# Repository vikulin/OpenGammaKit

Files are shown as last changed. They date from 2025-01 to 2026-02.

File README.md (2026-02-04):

# OpenGammaKit

## PCB front and back side

<table>
  <tr>
    <td align="center">
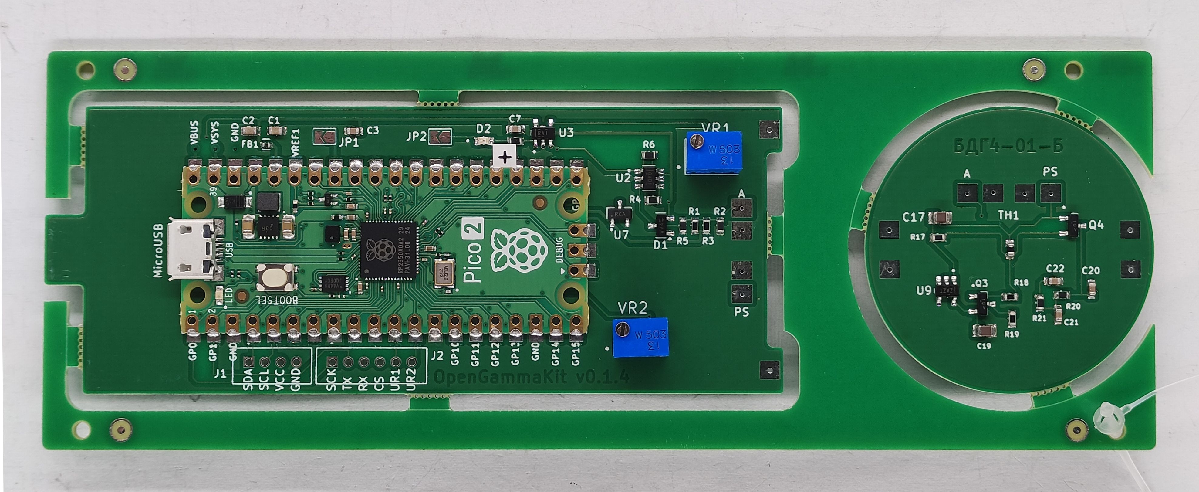
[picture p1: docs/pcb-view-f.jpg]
Front View of the detector board Front View
      
      <br><b>Front view</b>
    </td>
    <td align="center">
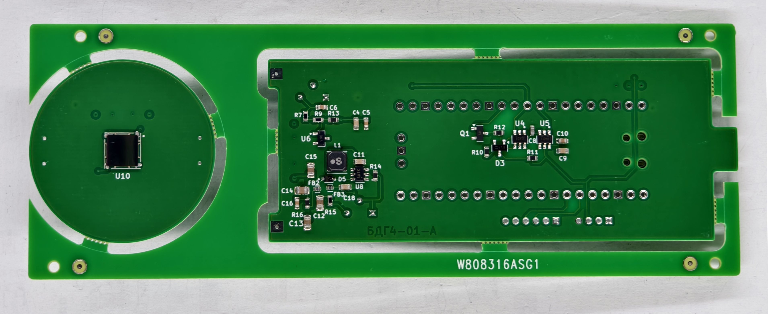
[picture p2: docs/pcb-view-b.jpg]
Back View of the detector board Back View
      
      <br><b>Back view</b>
    </td>
  </tr>
</table>

**OpenGammaKit** is an open-source gamma spectrometer hardware platform, inspired by the excellent [Open-Gamma-Detector](https://github.com/OpenGammaProject/Open-Gamma-Detector). It takes the original schematic and redesigns the PCB using **KiCad** (originally designed in EasyEDA), making the project more accessible and modifiable for open hardware enthusiasts.

OpenGammaKit is designed to be affordable, reliable, and easy to integrate with embedded systems, mobile devices, or PCs—ideal for DIY nuclear instrumentation, educational labs, or citizen science.

---

## Order the PCB or PCB + Assembly

You can order the **Open Gamma Kit** PCB or a fully assembled board directly from PCBWay using the link below:

Order from PCBWay (https://www.pcbway.com/project/shareproject/W808316ASG1_open_gamma_kit_gerber_files_v0_1_4_2_90620442.html)

👉 [Order PCB or PCB + Assembly from PCBWay](https://www.pcbway.com/project/shareproject/W808316ASG1_open_gamma_kit_gerber_files_v0_1_4_2_90620442.html)

This helps support the project and ensures high-quality manufacturing.

---

## 🔧 Features

- ✅ Based on the **Open-Gamma-Detector** schematic  
- ✅ Complete redesign in **KiCad** with improved layout and routing  
- ✅ USB serial communication (compatible with Android 7.0+ and PCs)  
- ✅ Compatible with [OGK Inspector](https://github.com/vikulin/OGK-Inspector) Android app and [OGK Firmware](https://github.com/vikulin/OGK-Firmware) 
- ✅ Real-time gamma spectrum output and spectrometer integration  
- ✅ Works with scintillation detectors (e.g., CsI(Tl), NaI(Tl), etc.)  
- ✅ Open and editable source files for schematics and PCB

---

## 📘Assembly guide, 3D models for enclosure

https://github.com/vikulin/OGK-3D-Models

---

## 📂 Repository Contents

- `/docs/` – Spectrum([OGK Inspector](https://github.com/vikulin/OGK-Inspector))
- `/kicad-libraries/` – KiCad libraries, including custom footprints

---

## 📷 3D render previews of the boards

<p align="center">
  <br>
  3d Front View of the detector board
  <br>
  3d Back View of the detector board
</p>

---

## 📦 Release Contents

OpenGammaKit releases version **0.1.5.5** and later include all the fabrication files required to manufacture and assemble the OpenGammaKit gamma spectrometer hardware:

| File Name                                     | Description                                                                |
| --------------------------------------------- | -------------------------------------------------------------------------- |
| `open-gamma-kit-gerber-files-<version>.zip`   | 🟢 Complete Gerber and Drill files for PCB fabrication.                    |
| `open-gamma-kit-centroid-file-<version>.csv`  | 📍 Centroid (Pick-and-Place) file in mils for automated assembly.          |
| `open-gamma-kit-<version>.pdf`                | 📄 PDF documentation                                                       |
| `BOM.csv`                                     | 📋 Bill of Materials (not archived — listed separately).                   |

📁 **Location**: All files are available in the [Assets](https://github.com/vikulin/OpenGammaKit/releases) release section.

---

## 🧠 Companion Projects

- **OGK Inspector (Android App)**  
  View spectra, calculate resolution, access terminal mode  
  👉 [OGK-Inspector on GitHub](https://github.com/vikulin/OGK-Inspector)

- **OGK Firmware**  
  USB serial interface firmware for supported microcontrollers  
  👉 [OGK Firmware Repository](https://github.com/vikulin/OGK-Firmware)

---

## Spectrum of ²⁴¹Am source measured with NaI(Tl) detector
| Element | Symbol | Atomic Number | Mass Number |
|---------|--------|----------------|--------------|
| Americium | Am     | 95             | 241          |

The spectrum clearly shows two gamma peaks at **59.54 keV** and **26.35 keV**, both corresponding to emissions from ²⁴¹Am:

- The **59.54 keV** peak is the most intense and commonly used for energy calibration.
- The **26.35 keV** peak is weaker but still visible, depending on detector resolution and shielding conditions.

<p align="center">
  <br>
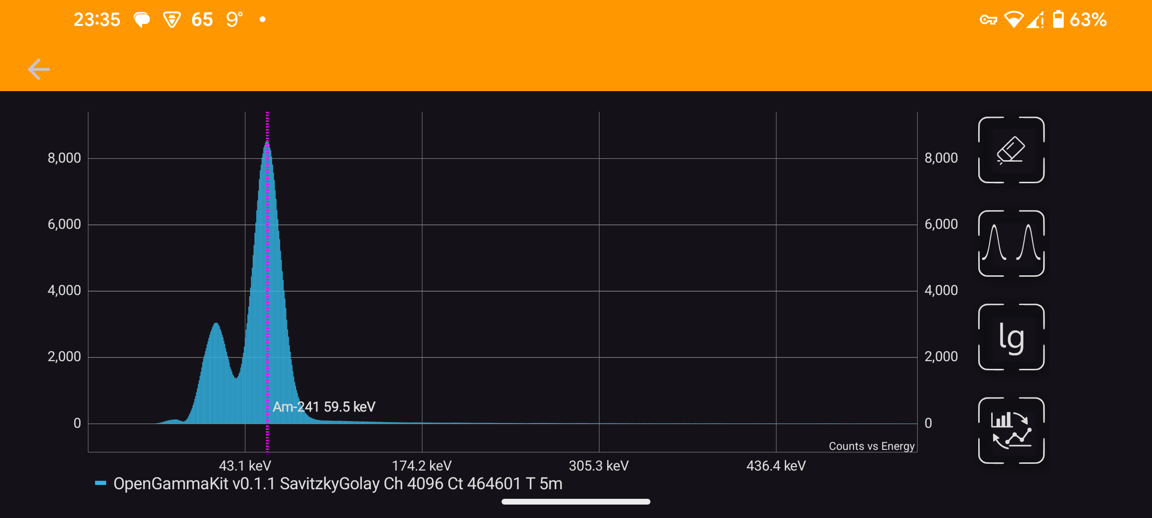
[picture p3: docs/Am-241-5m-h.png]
Am-241 Am-241 10 minutes spectrum
  
</p>

> 📌 These lines are useful for calibration and spectral identification in low-energy gamma spectroscopy using NaI(Tl) detectors.

---

## 📜 License

This project is licensed under the **GNU General Public License v3.0**.  
See the [LICENSE](LICENSE) file for details.

---

## 🙌 Acknowledgements

- Based on the original design by [OpenGammaProject](https://github.com/OpenGammaProject/Open-Gamma-Detector)  
- Thanks to the open hardware and spectroscopy communities!

---

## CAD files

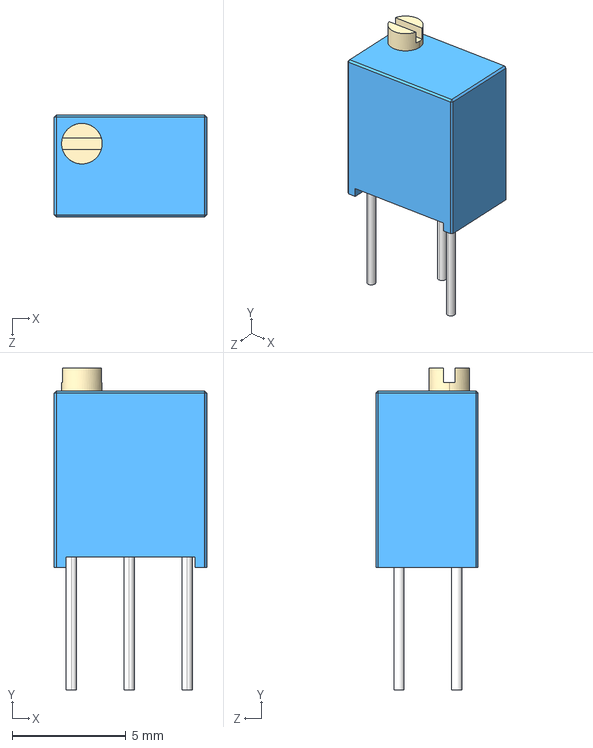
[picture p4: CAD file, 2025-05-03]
kicad-libraries/3266W-1-503/3266W-1-503.step
6.71 x 14.1 x 4.50 mm

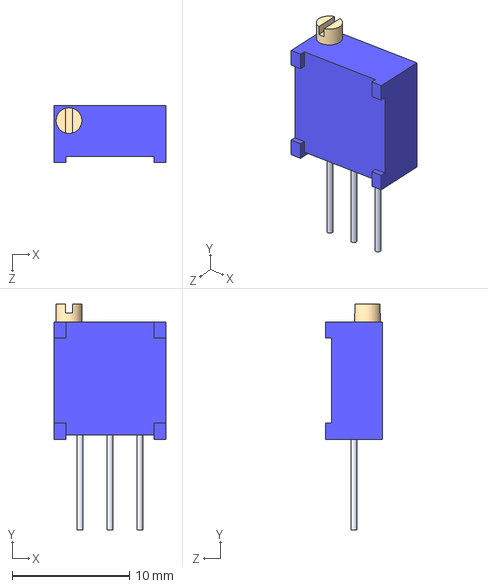
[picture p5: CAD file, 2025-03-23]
kicad-libraries/3296W-1-502LF/3296W-1-502LF.step
9.53 x 19.3 x 4.83 mm

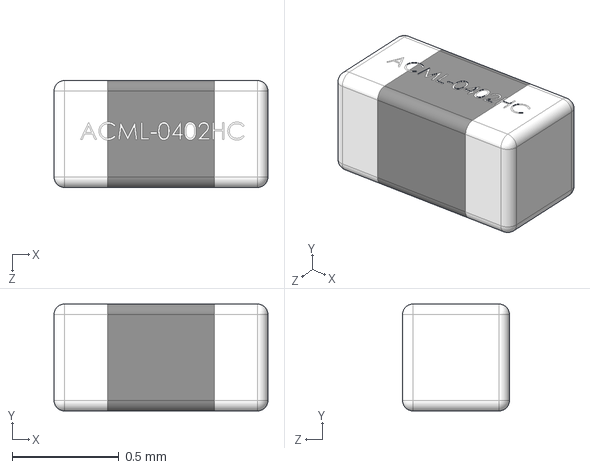
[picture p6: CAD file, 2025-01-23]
kicad-libraries/ACML-0402HC-301-T/ACML-0402HC-301-T.step
1.00 x 0.5 x 0.5 mm

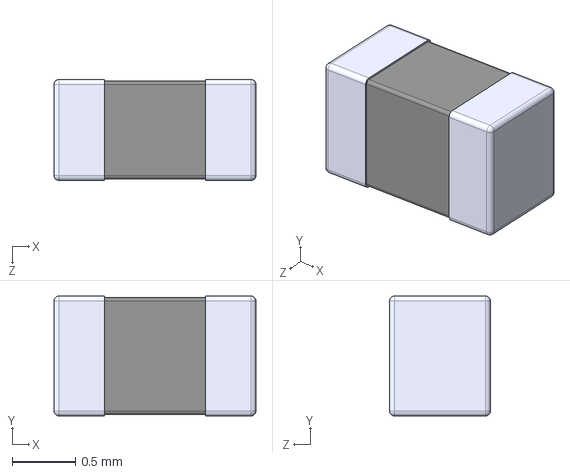
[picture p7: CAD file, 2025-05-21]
kicad-libraries/BLM18KG102SN1D/BLM18KG102SN1D.step
1.60 x 0.95 x 0.8 mm

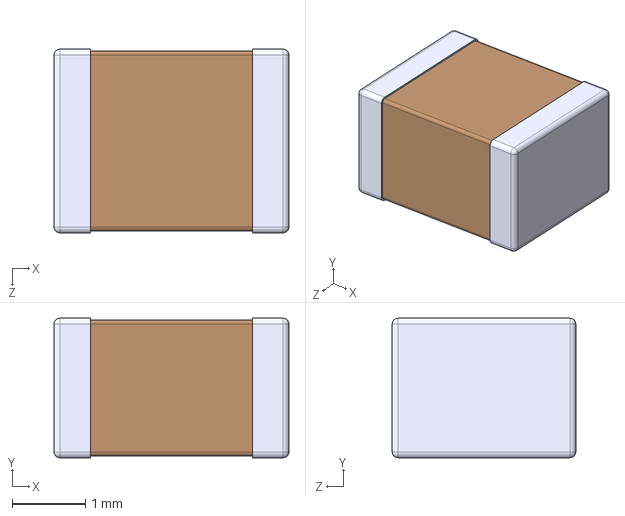
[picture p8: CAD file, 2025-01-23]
kicad-libraries/C1210C104KCRACTU/C1210C104KCRACTU.step
3.20 x 1.90 x 2.50 mm

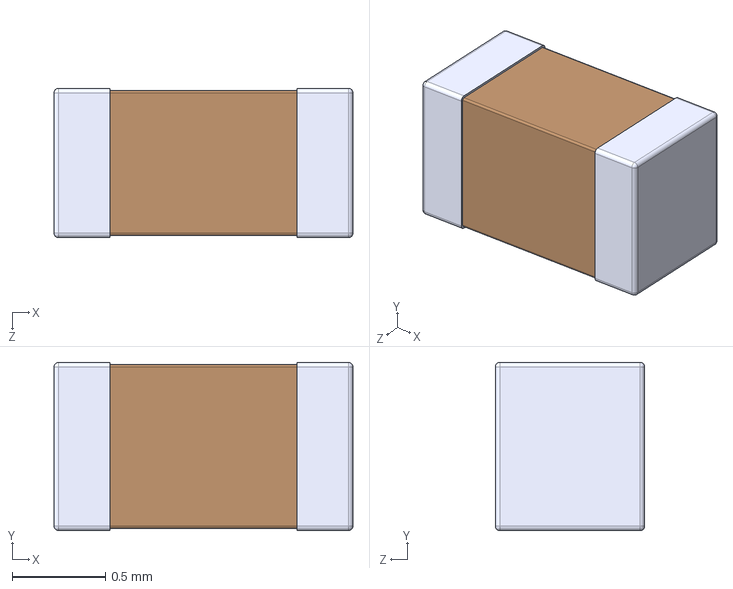
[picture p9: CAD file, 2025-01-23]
kicad-libraries/CL10A226MP8NUNE/CL10A226MP8NUNE.step
1.60 x 0.9 x 0.8 mm

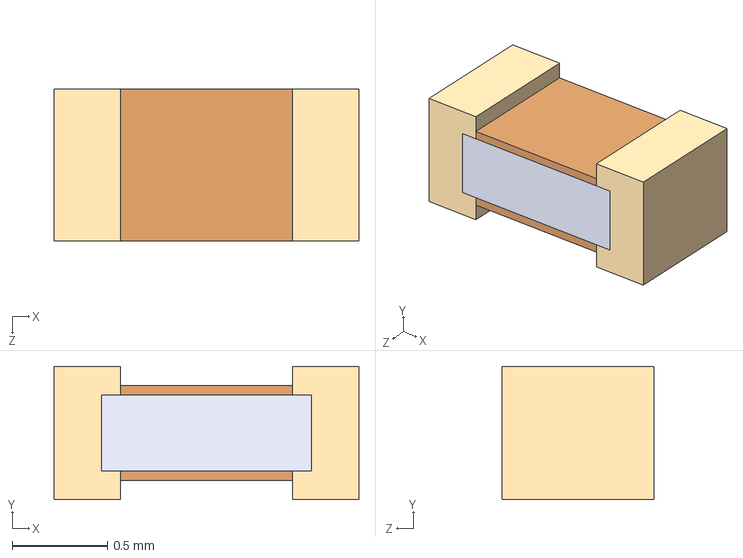
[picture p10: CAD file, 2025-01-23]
kicad-libraries/ECHU1C471JX5/ECHU1C471JX5.step
1.60 x 0.7 x 0.8 mm

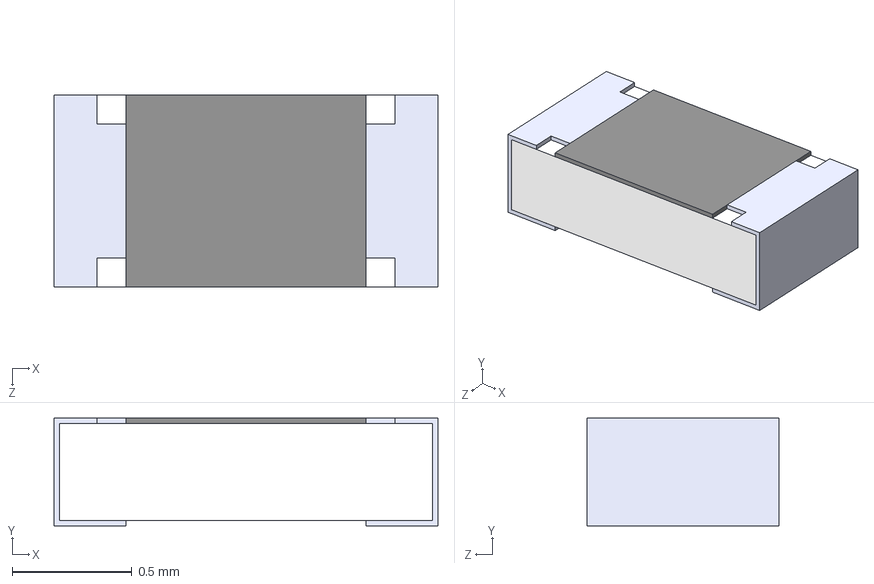
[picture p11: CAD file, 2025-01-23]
kicad-libraries/ERJ3EKF1000V/ERJ3EKF1000V.step
1.60 x 0.45 x 0.8 mm

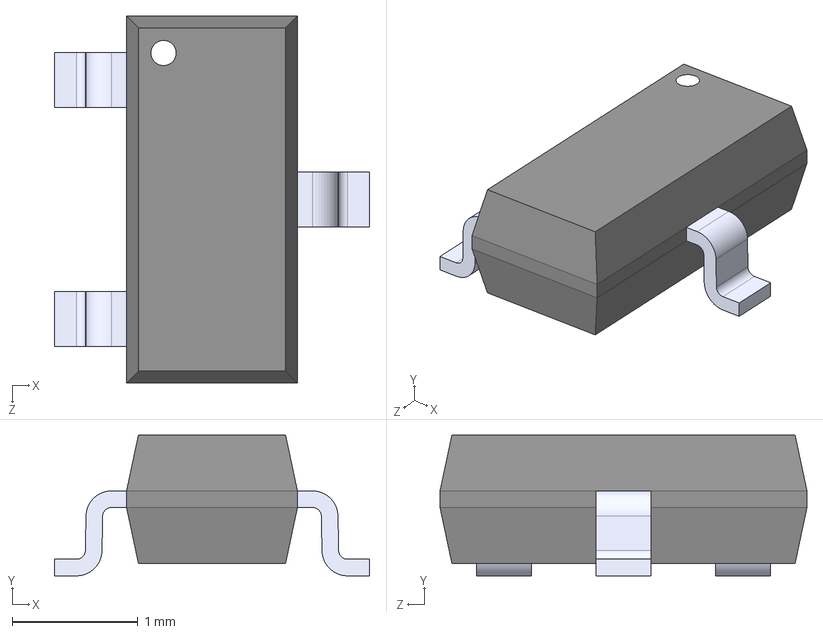
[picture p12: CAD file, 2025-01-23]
kicad-libraries/IRLML6344TRPBF/IRLML6344TRPBF.step
2.51 x 1.12 x 2.92 mm

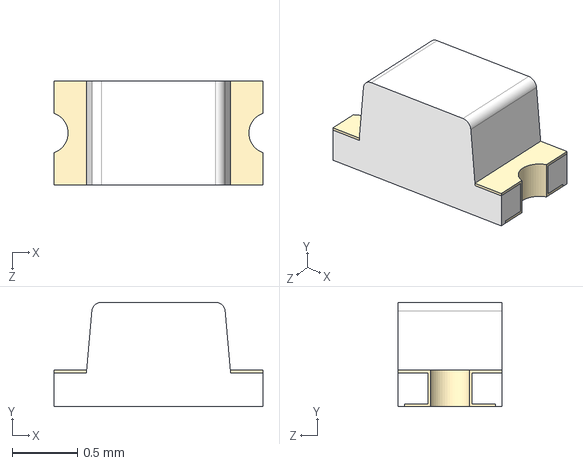
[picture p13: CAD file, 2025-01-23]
kicad-libraries/LTST-C190KGKT/LTST-C190KGKT.step
1.60 x 0.8 x 0.8 mm

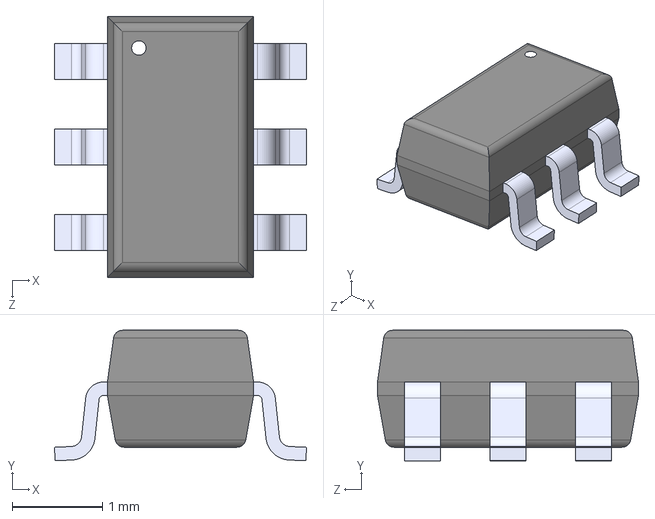
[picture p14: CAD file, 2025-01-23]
kicad-libraries/MAX5026EUT_T/MAX5026EUT_T.step
2.80 x 1.45 x 2.90 mm

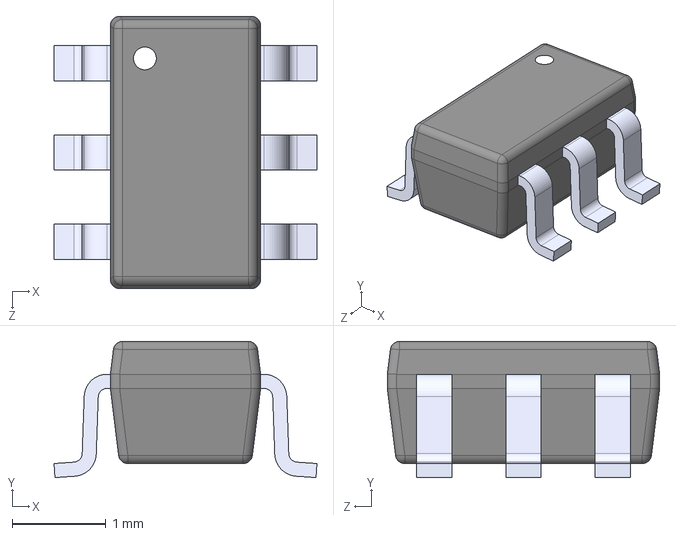
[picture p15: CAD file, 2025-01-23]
kicad-libraries/OPA357AIDBVR/OPA357AIDBVR.step
2.80 x 1.45 x 2.90 mm

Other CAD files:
kicad-libraries/20449-001E-03/20449-001E-03.step
kicad-libraries/MMBT5088LT1G/MMBT5088LT1G.step
kicad-libraries/NRS4018T470MDGJ/NRS4018T470MDGJ.step
kicad-libraries/TPS7B6950DBVR/TPS7B6950DBVR.step
kicad-libraries/TPS7B6950QDCYRQ1/TPS7B6950QDCYRQ1.step
kicad-libraries/ul_AST0760MCTRQ/AltiumDesigner/AST0760_MAL.step

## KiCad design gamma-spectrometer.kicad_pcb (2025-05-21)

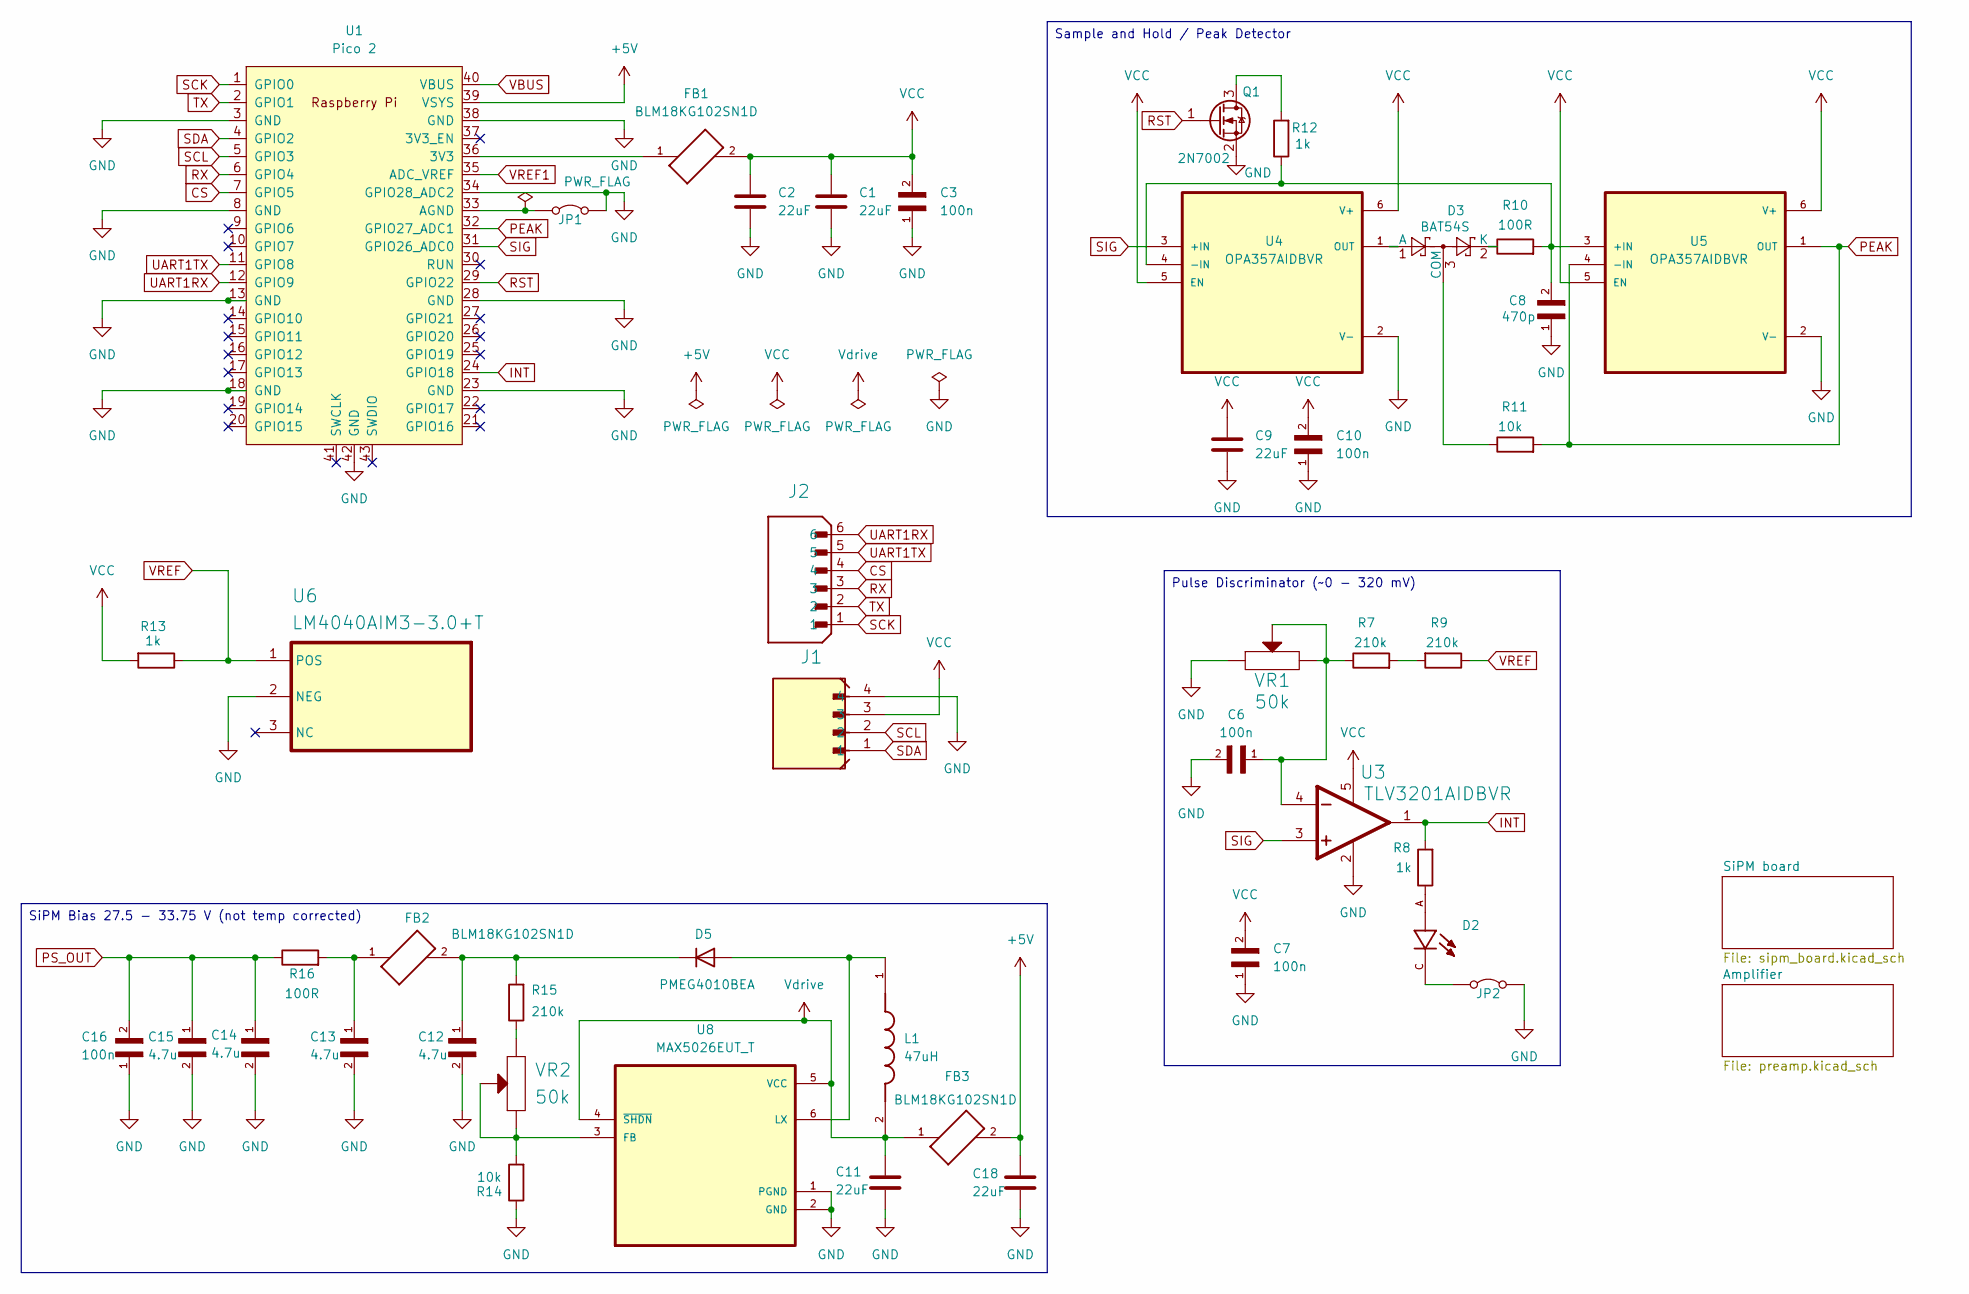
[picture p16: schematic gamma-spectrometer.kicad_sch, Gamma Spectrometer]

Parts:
C1, C2, C9, C11, C18: 22uF; CAPC1608X90N
C3, C6, C7, C10, C16: 100n; CAPC1608X90N; PARTREV NA
C8: 470p; CAP_ECHU1C471JX5; PARTREV 11-Oct-17
C12, C13, C14, C15: 4.7u; CAPC2012X140N
D2: LTST-C190KGKT; LEDC1608X35N
D3: BAT54S; SOT-23
D5: PMEG4010BEA; DIO_BZX384-C30_115
FB1, FB2, FB3: BLM18KG102SN1D; BEADC1608X95N
J1: *; JST_B4B-PH-K-S(LF)(SN)
J2: *; JST_B6B-PH-K-S(LF)(SN)
JP1, JP2: SolderJumper-2_P1.3mm_Open_TrianglePad1.0x1.5mm
L1: 47uH; IND_NRS4018T470MDGJ; PARTREV 2021.10.25
Q1: 2N7002; SOT-23
R7, R9, R15: 210k; RES_ERJ3EKF2103V
R8, R12, R13: 1k; RES_ERJ3EKF1001V
R10, R16: 100R; RES_ERJ3EKF1000V
R11, R14: 10k; RES_ERJ3EKF1002V
U1: Pico 2; RPi_Pico_SMD_TH
U3: TLV3201AIDBVR; SOT95P280X145-5N
U4, U5: OPA357AIDBVR; SOT95P280X145-6N
U6: LM4040AIM3-3.0+T; SOT95P237X112-3N
U8: MAX5026EUT_T; SOT95P280X145-6N
VR1, VR2: 50k; TRIM_3266W-1-503

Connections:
+5V: C18.1, FB3.2, U1.39 (VSYS)
CS: J2.4, U1.7 (GPIO5)
GND: C1.2, C2.2, C3.1, C6.2, C7.1, C8.1, C9.2, C10.1, C11.2, C12.2, C13.2, C14.2, C15.2, C16.1, C18.2, J1.4, JP1.2 (B), JP2.2 (B), Q1.2 (S), R14.1, U1.3 (GND), U1.8 (GND), U1.13 (GND), U1.18 (GND), U1.23 (GND), U1.28 (GND), U1.34 (GPIO28_ADC2), U1.38 (GND), U1.42 (GND), U3.2 (GND), U4.2 (V-), U5.2 (V-), U6.2 (NEG), U8.1 (PGND), U8.2 (GND), VR1.1 (CCW); also elsewhere on the board
INT: R8.2, U1.24 (GPIO18), U3.1 (OUT)
unnamed: C13.1, FB2.1, R16.2
unnamed: D2.A, R8.1
unnamed: D3.1 (A), U4.1 (OUT)
unnamed: D3.3 (COM), R11.1
unnamed: D3.2 (K), R10.1
unnamed: D5.2 (A), L1.1, U8.6 (LX)
unnamed: C12.1, D5.1 (K), FB2.2, R15.2
unnamed: JP1.1 (A), U1.33 (AGND)
unnamed: D2.C, JP2.1 (A)
unnamed: Q1.3 (D), R12.2
unnamed: R7.2, R9.2
unnamed: FB1.1, U1.36 (3V3)
unnamed: C6.1, R7.1, U3.4 (IN-), VR1.2 (WIPER), VR1.3 (CW)
unnamed: C8.2, R10.2, R12.1, U4.4 (-IN), U5.3 (+IN)
unnamed: R14.2, U8.3 (FB), VR2.1 (CCW), VR2.2 (WIPER)
unnamed: R15.1, VR2.3 (CW)
PEAK: R11.2, U1.32 (GPIO27_ADC1), U5.1 (OUT), U5.4 (-IN)
PS_OUT: C14.1, C15.1, C16.2, R16.1
RST: Q1.1 (G), U1.29 (GPIO22)
RX: J2.3, U1.6 (GPIO4)
SCK: J2.1, U1.1 (GPIO0)
SCL: J1.2, U1.5 (GPIO3)
SDA: J1.1, U1.4 (GPIO2)
SIG: U1.31 (GPIO26_ADC0), U3.3 (IN+), U4.3 (+IN); also elsewhere on the board
TX: J2.2, U1.2 (GPIO1)
UART1RX: J2.6, U1.12 (GPIO9)
UART1TX: J2.5, U1.11 (GPIO8)
VBUS: U1.40 (VBUS)
VCC: C1.1, C2.1, C3.2, C7.2, C9.1, C10.2, FB1.2, J1.3, R13.2, U3.5 (VCC), U4.5 (EN), U4.6 (V+), U5.5 (EN), U5.6 (V+); also elsewhere on the board
VREF: R9.1, R13.1, U6.1 (POS)
VREF1: U1.35 (ADC_VREF); also elsewhere on the board
Vdrive: C11.1, FB3.1, L1.2, U8.4 (~SHDN), U8.5 (VCC)

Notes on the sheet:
Pulse Discriminator (~0 - 320 mV)
Sample and Hold / Peak Detector
SiPM Bias 27.5 - 33.75 V (not temp corrected)

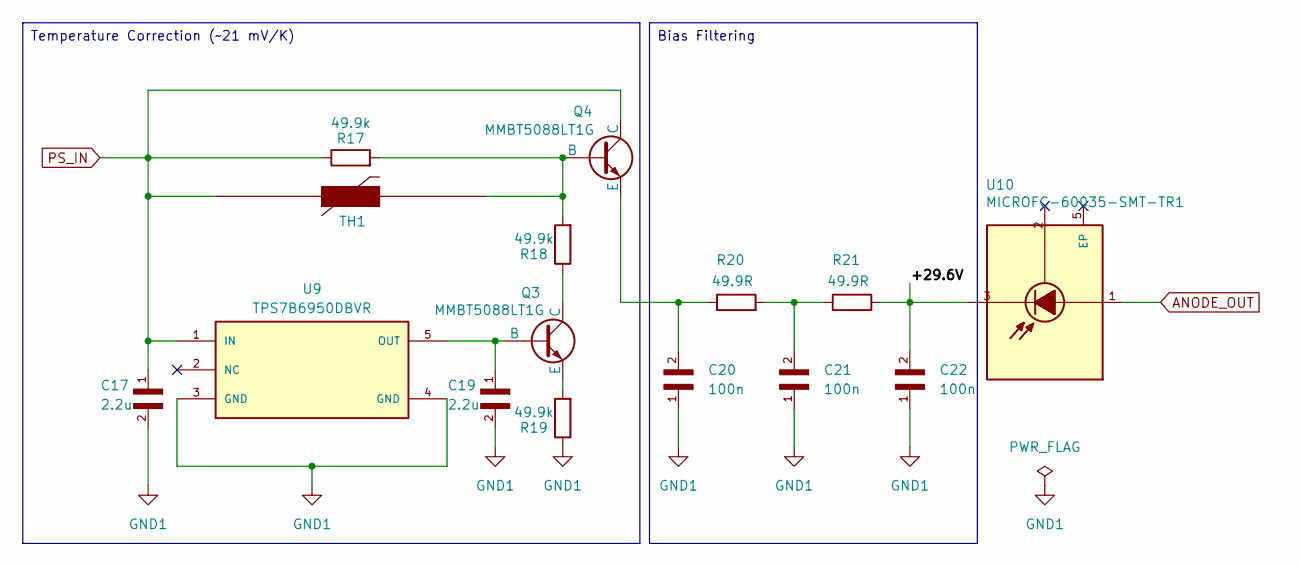
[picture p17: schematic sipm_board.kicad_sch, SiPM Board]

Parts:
C17, C19: 2.2u; C_0603_1608Metric
C20, C21, C22: 100n; CAPC1608X90N; PARTREV NA
Q3, Q4: MMBT5088LT1G; SOT95P237X111-3N
R17, R18, R19: 49.9k; RES_ERJ3EKF4992V
R20, R21: 49.9R; RES_ERJ3EKF49R9V
TH1: Thermistor_PTC; NTCS0603E3103FLT
U9: TPS7B6950DBVR; SOT95P280X145-5N
U10: MICROFC-60035-SMT-TR1; XDCR_MICROFC-60035-SMT-TR1; PARTREV 31 JUL 2018

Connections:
/SiPM board/+29.6V: C22.2, R21.2, U10.3
ANODE_OUT: U10.1
GND1: C17.2, C19.2, C20.1, C21.1, C22.1, R19.1, U9.3 (GND), U9.4 (GND)
unnamed: C21.2, R20.2, R21.1
unnamed: C19.1, Q3.2 (B), U9.5 (OUT)
unnamed: Q3.1 (C), R18.1
unnamed: Q3.3 (E), R19.2
unnamed: Q4.2 (B), R17.2, R18.2, TH1.1
unnamed: C20.2, Q4.3 (E), R20.1
PS_IN: C17.1, Q4.1 (C), R17.1, TH1.2, U9.1 (IN)

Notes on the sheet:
Bias Filtering
Temperature Correction (~21 mV/K)

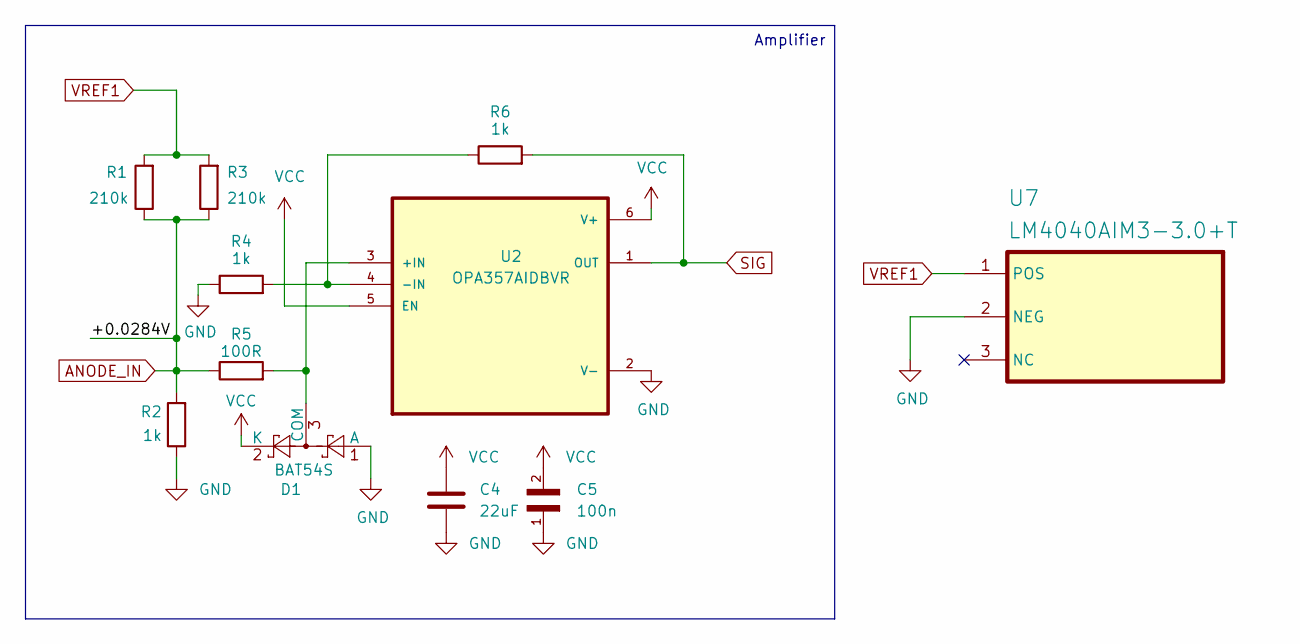
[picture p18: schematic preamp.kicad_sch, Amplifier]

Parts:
C4: 22uF; CAPC1608X90N
C5: 100n; CAPC1608X90N; PARTREV NA
D1: BAT54S; SOT-23
R1, R3: 210k; RES_ERJ3EKF2103V
R2, R4, R6: 1k; RES_ERJ3EKF1001V
R5: 100R; RES_ERJ3EKF1000V
U2: OPA357AIDBVR; SOT95P280X145-6N
U7: LM4040AIM3-3.0+T; SOT95P237X112-3N

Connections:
ANODE_IN: R1.1, R2.2, R3.1, R5.1
GND: C4.2, C5.1, D1.1 (A), R2.1, R4.1, U2.2 (V-), U7.2 (NEG); also elsewhere on the board
unnamed: D1.3 (COM), R5.2, U2.3 (+IN)
unnamed: R4.2, R6.1, U2.4 (-IN)
SIG: R6.2, U2.1 (OUT); also elsewhere on the board
VCC: C4.1, C5.2, D1.2 (K), U2.5 (EN), U2.6 (V+); also elsewhere on the board
VREF1: R1.2, R3.2, U7.1 (POS); also elsewhere on the board

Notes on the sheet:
Amplifier

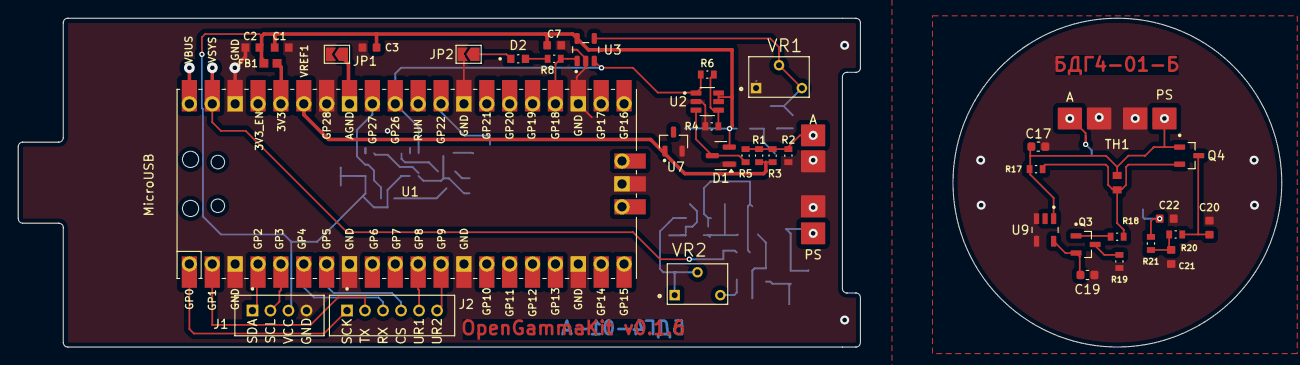
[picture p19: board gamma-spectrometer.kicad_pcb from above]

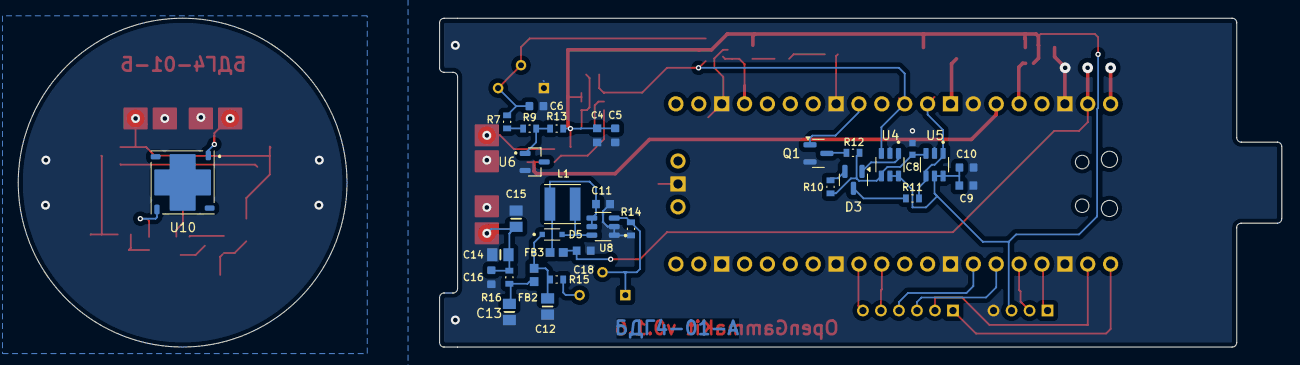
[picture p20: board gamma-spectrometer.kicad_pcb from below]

Board: 2 copper layers, 140.3 x 36.5 mm, 71 parts (33 on the bottom side), 47 nets.

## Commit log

2025-01-23 Removed obsolete file
    [high_voltage_power_supply.kicad_sch]
2025-01-23 Exclude autosave files
    [gamma-spectrometer.kicad_pcb]
2025-01-23 Added drl files
    [gamma-spectrometer-NPTH-drl.gbr, gamma-spectrometer-PTH-drl.gbr, gamma-spectrometer-backup.kicad_pcb]
2025-01-23 Corrected labels
    [gamma-spectrometer-B_Cu.gbr, gamma-spectrometer-B_Mask.gbr, gamma-spectrometer-B_Paste.gbr, gamma-spectrometer-B_Silkscreen.gbr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]
2025-01-24 Added schematic
    [gamma-spectrometer.kicad_sch]
2025-01-25 Exclude backup files
    [gamma-spectrometer-backup.kicad_pcb]
2025-01-26 U8 5-6 pins connection error fix
    [gamma-spectrometer-B_Cu.gbr, gamma-spectrometer-B_Mask.gbr, gamma-spectrometer-B_Paste.gbr, gamma-spectrometer-B_Silkscreen.gbr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]
2025-01-26 D1 1-2 pins conenction error fix
    [gamma-spectrometer-B_Cu.gbr, gamma-spectrometer-B_Mask.gbr, gamma-spectrometer-B_Paste.gbr, gamma-spectrometer-B_Silkscreen.gbr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]
2025-01-26 U2 GNS connection error fix
    [gamma-spectrometer-B_Cu.gbr, gamma-spectrometer-B_Mask.gbr, gamma-spectrometer-B_Paste.gbr, gamma-spectrometer-B_Silkscreen.gbr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]
2025-02-09 PCB size fix
    PCB size fix
    Zoomer position adjustment
    Minor fixes
    Centered U1
    PCB view update
    [gamma-spectrometer-B_Cu.gbr, gamma-spectrometer-B_Mask.gbr, gamma-spectrometer-B_Paste.gbr, gamma-spectrometer-B_Silkscreen.gbr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]
2025-02-12 Added BOM
    [BOM.csv]
2025-02-19 C3 duplication fix
    [BOM.csv, gamma-spectrometer-B_Cu.gbr, gamma-spectrometer-B_Mask.gbr, gamma-spectrometer-B_Paste.gbr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]
2025-02-26 Changed schematic for default I2C pins
    [BOM.csv, gamma-spectrometer-B_Cu.gbr, gamma-spectrometer-B_Mask.gbr, gamma-spectrometer-B_Paste.gbr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]
2025-03-07 Added gain regulator. MHF3 connector for signal line.
    [20449-001E-03.step, 3296W-1-502LF.step, BOM.csv, gamma-spectrometer-B_Cu.gbr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]
2025-04-02 BDG4-01 module boards design
    [BOM.csv, gamma-spectrometer-B_Cu.gbr, gamma-spectrometer-B_Mask.gbr, gamma-spectrometer-B_Paste.gbr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]
2025-04-03 PCB changes for more precise assembling
    [gamma-spectrometer-B_Cu.gbr, gamma-spectrometer-B_Mask.gbr, gamma-spectrometer-B_Paste.gbr, gamma-spectrometer-B_Silkscreen.gbr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]
2025-04-25 Important fix for SiPM power supply circuit. Moved gerber files.
    [gamma-spectrometer-B_Cu.gbr, gamma-spectrometer-B_Mask.gbr, gamma-spectrometer-B_Paste.gbr, gamma-spectrometer-B_Silkscreen.gbr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]
2025-04-26 Updated BOM, schematic , foortprints, symbols
    [BOM.csv, ERJ3EKF1000V.step, ERJ3EKF1001V.step, ERJ3EKF1002V.step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]
2025-04-26 Minor changes
    [gamma-spectrometer-B_Cu.gbr, gamma-spectrometer-B_Mask.gbr, gamma-spectrometer-B_Paste.gbr, gamma-spectrometer-B_Silkscreen.gbr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]
2025-05-01 Removed VR2 resistor and adjusted R6 to prevent self-oscillation of the amplifier
    [gamma-spectrometer-B_Cu.gbr, gamma-spectrometer-B_Mask.gbr, gamma-spectrometer-B_Paste.gbr, gamma-spectrometer-B_Silkscreen.gbr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]
2025-05-01 Updated BOM
    [BOM.csv]
2025-05-03 Update packages for smaller size for VR1,VR2
    [3266W-1-503.step, BOM.csv, gamma-spectrometer-B_Cu.gbr, gamma-spectrometer-B_Mask.gbr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]
2025-05-05 Updated BOM format accordingly to PCBWay format
    [BOM.csv, gamma-spectrometer-B_Cu.gbr, gamma-spectrometer-B_Mask.gbr, gamma-spectrometer-B_Paste.gbr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]
2025-05-06 Centroid files for PCBWay fabrication
2025-05-06 Automatic generation fabrication output files such as Gerber, Drill and Centroid
    [gamma-spectrometer-B_Cu.gbr, gamma-spectrometer-B_Mask.gbr, gamma-spectrometer-B_Paste.gbr, gamma-spectrometer-B_Silkscreen.gbr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]
2025-05-06 Automatic generation fabrication output files such as Gerber, Drill and Centroid. Updated README.
    [gamma-spectrometer-B_Cu.gbr, gamma-spectrometer-B_Mask.gbr, gamma-spectrometer-B_Paste.gbr, gamma-spectrometer-B_Silkscreen.gbr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]
2025-05-06 Corrected BOM, Automated Gerber and Docs generation for release, bump version
    BOM generation is remaining manual
    Corrected manufacturer part#
    Update build.yml
    [BOM.csv, gamma-spectrometer.kicad_pcb, gamma-spectrometer.kicad_sch, preamp.kicad_sch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]
2025-05-06 Migrated to KiCad 9.0
    [BOM.csv, gamma-spectrometer.kicad_pcb, gamma-spectrometer.kicad_sch, preamp.kicad_sch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]
2025-05-08 PCBWay BOM generation preset
    [BOM.csv]
2025-05-08 ERC errors fix
    [gamma-spectrometer.kicad_sch, preamp.kicad_sch, sipm_board.kicad_sch]
2025-05-08 Excluded from BOM
    [gamma-spectrometer.kicad_sch]
2025-05-08 ERC test
    [gamma-spectrometer.kicad_pcb, gamma-spectrometer.kicad_sch, preamp.kicad_sch, sipm_board.kicad_sch]
2025-05-08 Power flags fix
    [gamma-spectrometer.kicad_sch]
2025-05-08 Minor change in schematic
    [sipm_board.kicad_sch]
2025-05-18 PCB preview image dimensions adjustment
2025-05-21 C17,C19,FB1,FB2,FB3 footprint fix
    [BLM18KG102SN1D.step, gamma-spectrometer.kicad_pcb, gamma-spectrometer.kicad_sch, sipm_board.kicad_sch]
2025-05-30 PCB view update
2026-02-04 Add assembly guide and 3D models link
    Added assembly guide and 3D models section to README.
